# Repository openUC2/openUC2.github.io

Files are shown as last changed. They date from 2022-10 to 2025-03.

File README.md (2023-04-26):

# openUC2 Documentation

This is the repository where you will find all kinds of documents, tutorials and helping functions to get started with UC2.

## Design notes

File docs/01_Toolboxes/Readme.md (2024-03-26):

# Educational Kits

## CoreBox: Entry-Level Education Box
     - Features and Specifications
     - Assembling the CoreBox
     - Core Lens, Telescope, and Microscope

## Discovery Kit: Extension of CoreBox
     - Adding Modules to the Discovery Kit
     - Enhanced Functionality

## Interferometer Kit 
     - You can build a Michelson Interferometer
     - Try enhancing it to become a MAch Zhender Microscope 
     - Ultimatively test the microscope extension and reconstruct images using holography
     -

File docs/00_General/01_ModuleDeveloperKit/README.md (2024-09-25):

# openUC2 Template for your own Insert

We try to keep UC2 as open as possible. One important step is to give you the tools at hand to create your own insert in Order to add own functionalities, parts, modules, etc.
This repository should help you creating inserts and understand the core idea behind the shape and how it can be used to add e.g. lenses, mirros, motors.

If you have a more complex idea for a module, say a rotating diffuser, please feel free to reach out to us! We are happy to support your research with open-source tools!

A good resource is also the [***Module Developer Kit (MDK)***](https://github.com/openUC2/UC2-GIT/tree/master/MDK) that summarizes the core concept of UC2's modularity.

***What you will see here:***

* UC2 Cube Inserts
* Design files for
	* Autodesk Inventor
	* OpenSCAD
	* Fusion360
	* STP- and STL-files
* Technical drawings to replicate module in e.g. metal?
* Tutorial to design your modules in Autodesk

## UC2 v3 Design

## Fusion360 Design Files

### Cube and Base

This is a close-to-the-injection-molding design. The press-fit can vary. It's optimized for 3D printing.

You can find the latest Inventor Design files in the Fusion360 cloud: https://a360.co/3ZwHhl7

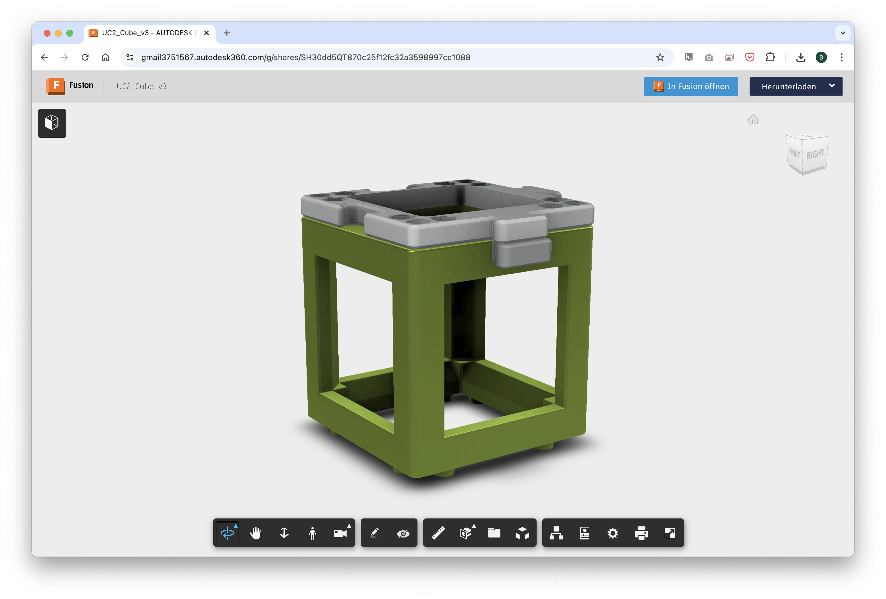
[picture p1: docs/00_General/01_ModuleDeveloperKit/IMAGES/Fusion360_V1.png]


You can download and export this in multiple CAD formats.

### Insert

This serves as a template for your optics. Fill it with whatever you have and model it in your 3D CAD software: https://a360.co/3MYo0RX

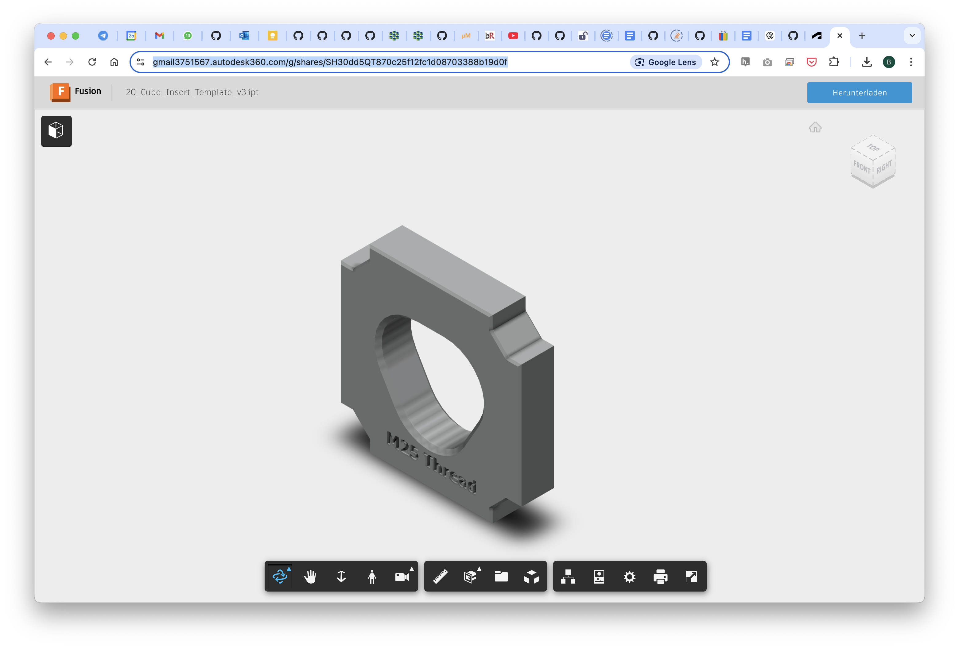
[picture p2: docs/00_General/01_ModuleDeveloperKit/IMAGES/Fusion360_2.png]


### UC2 Cube Inserts

The cube inserts can be fully customized to adapt any optical element to the cubes. So far a perpendicular and diagonal version exists. The design files for Autodesk Inventor and OpenSCAD are available. Once you have a customized version, please share it so that the open-aspect of the system reaches its full potential :)

A Youtube tutorial showing you how to create your own insert can be found [here](https://youtu.be/CUzuymscB5k)

Since the cube is point symmetric around the origin, the inserts can be rotated in all directions and bridges external components to the modules by acting as an open-standard.

When you create a new insert, you have to make sure it follows the following design criteria (e.g. dimensions):

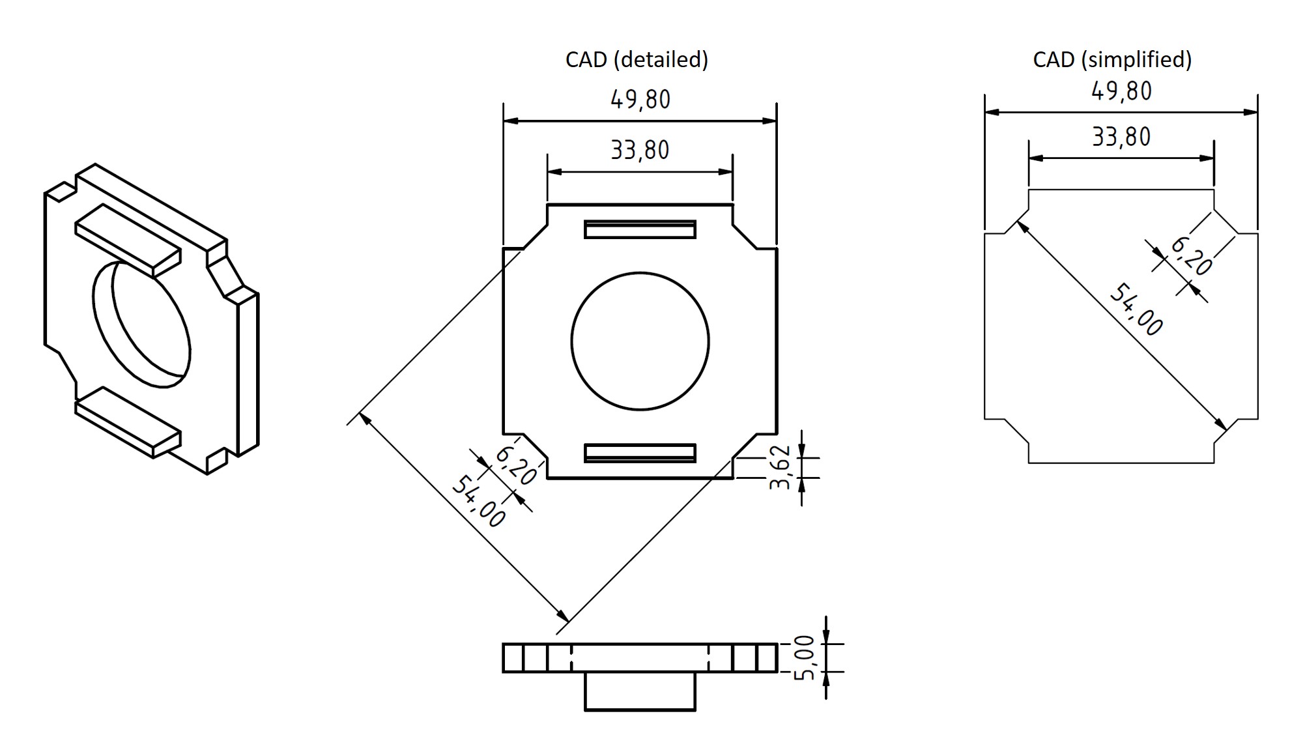
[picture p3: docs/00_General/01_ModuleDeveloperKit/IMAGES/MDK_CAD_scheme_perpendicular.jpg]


For the baseplate you must follow these dimensions:

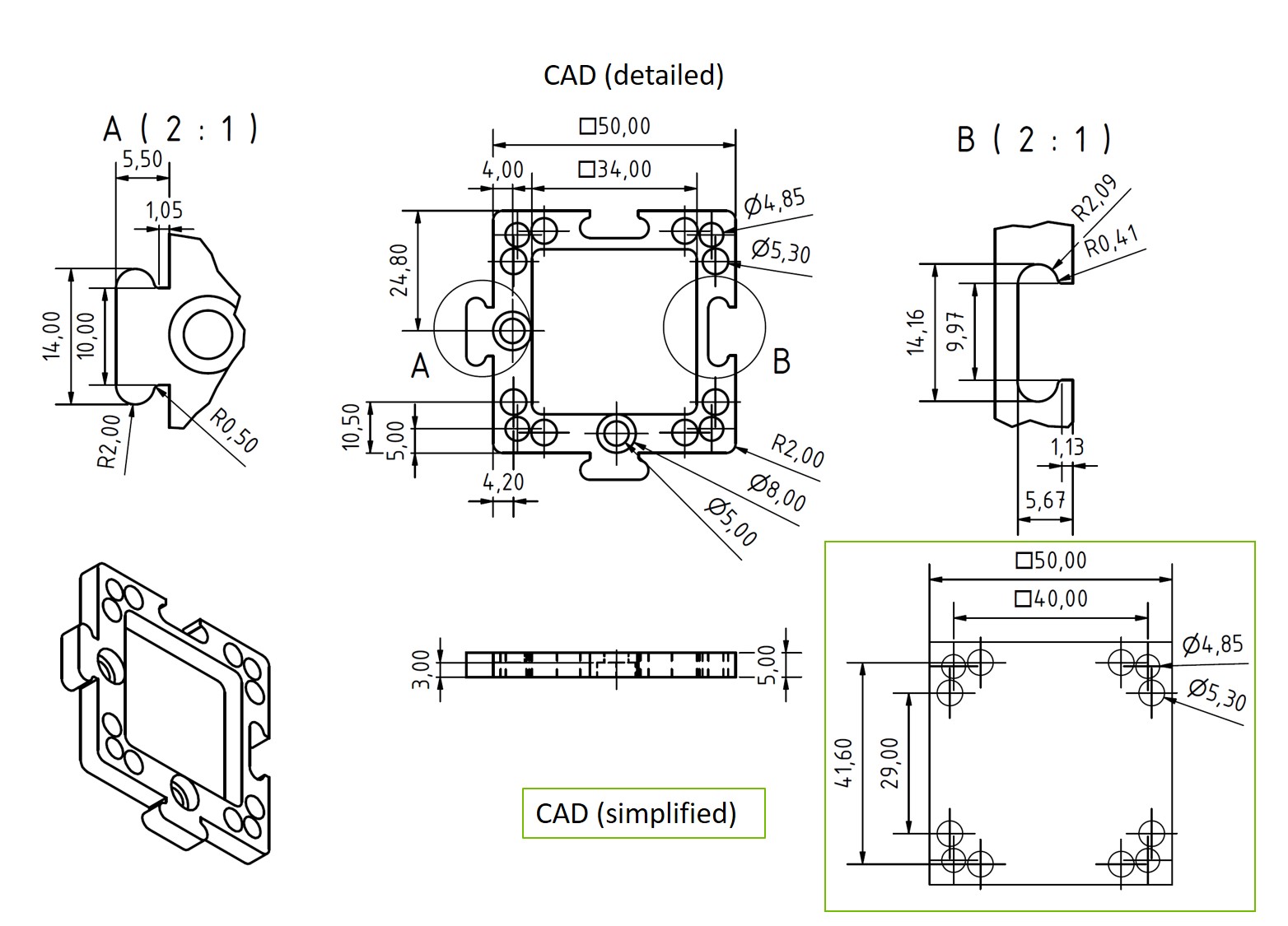
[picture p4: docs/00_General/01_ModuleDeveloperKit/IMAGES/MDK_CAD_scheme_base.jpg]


The CAD templates for Autodesk Inventor 2022 (```.ipt```) and ```STL/STEP```-standard can be found in the [INVENTOR](./INVENTOR)-folder and  [STL](./STL)/ [STP](./STP)-folder .

## Autodesk Inventor 2022 Design files

All files can be found in the folder [INVENTOR](./INVENTOR).

***Steps to work on the files:***

1. Open Autodesk Inventor 2022
2. Create a new project
3. Open the Assembly file: `Assembly_Cube_Template_v3.iam`
4. Get yourself familiar with the:
- Cube
- Baseplate
- Insert
5. Try modifying the file `20_Cube_Insert_Template_v3.ipt` so that you can mount your inidividual files

### Videotutorial

We have a dedicated video tutorial to show how you can create your own insert.
**Video Tutorial on How to design a Cube Insert (Perpendicular to the optical axis)**  
**The tutorial shows a v2 insert - the principle is the same but the dimensions differ!**

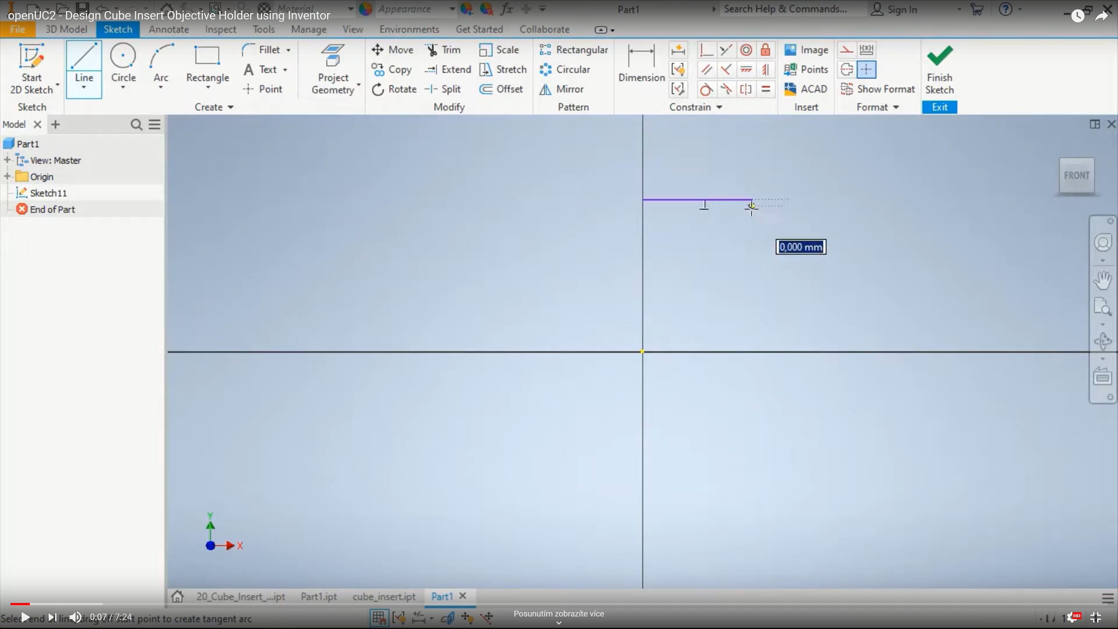
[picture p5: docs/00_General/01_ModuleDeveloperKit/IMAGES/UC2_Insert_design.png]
UC2 YouSeeToo - How to design an insert (https://www.youtube.com/watch?v=q2DNw-Q1KEo&t=2s)


## OpenSCAD Design files

All files can be found in the folder [OPENSCAD](./OPENSCAD).

*Alternatively* you can also find the files in the Thingiverse Universe that allows you to modify certain parameters in the file without installing openSCAD. You can find it here [Thingiverse](https://www.thingiverse.com/openuc2/designs).

***Steps to work on the files:***

1. Open OpenSCAD
2. Open the file `UC2_Lens_insert_v2.scad`
3. Try to understand what each parameter modifies in the geometry of the cube insert
4. Render and export as STL

## Technical Drawings

You can find additional information about the cube in the folder [CAD](./CAD).

### CAD file for the cube (injection molded / IM)

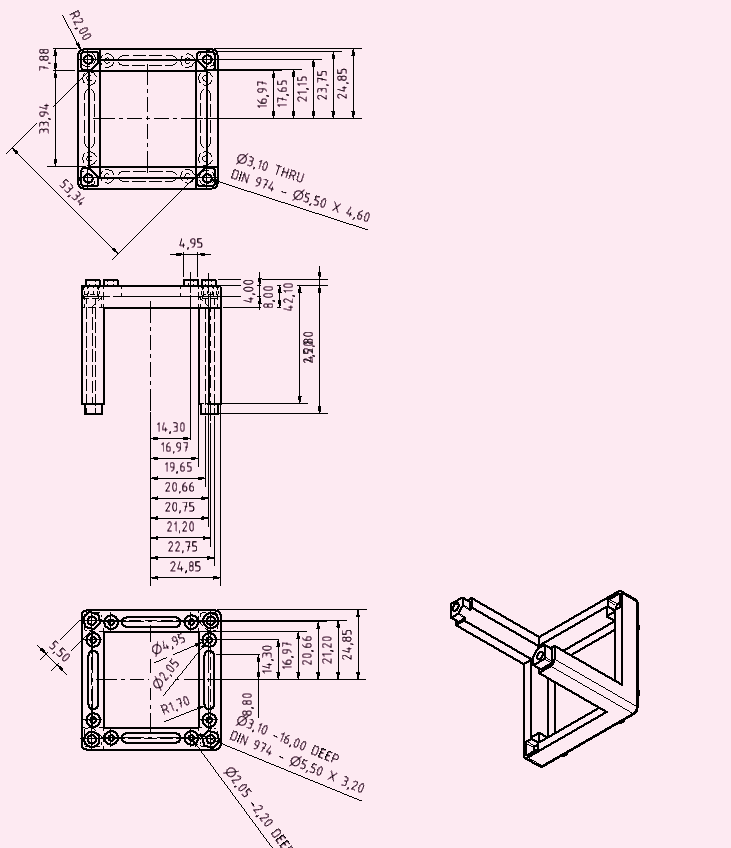
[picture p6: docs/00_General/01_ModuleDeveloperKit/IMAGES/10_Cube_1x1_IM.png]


## Get Involved

This project is open so that anyone can get involved. You don't even have to learn CAD designing or programming. Find ways you can contribute in  [CONTRIBUTING](https://github.com/openUC2/UC2-GIT/blob/master/CONTRIBUTING.md)

## License and Collaboration

This project is open-source and is released under the CERN open hardware license. Our aim is to make the kits commercially available.
We encourage everyone who is using our Toolbox to share their results and ideas, so that the Toolbox keeps improving. It should serve as a easy-to-use and easy-to-access general purpose building block solution for the area of STEAM education. All the design files are generally for free, but we would like to hear from you how is it going.

You're free to fork the project and enhance it. If you have any suggestions to improve it or add any additional functions make a pull-request or file an issue.

Please find the type of licenses [here](https://github.com/openUC2/UC2-GIT/blob/master/License.md)

REMARK: All files have been designed using Autodesk Inventor 2019 (EDUCATION)

## Collaborating
If you find this project useful, please like this repository, follow us on Twitter and cite the webpage! :-)

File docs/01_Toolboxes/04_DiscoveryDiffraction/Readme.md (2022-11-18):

# Building The CourseBOX

This is a guide for building the [CourseBOX](../). If you were looking for another BOX version, [click here](../../).

This guide currently describes how to build both the [finite-corrected version](#finite-corrected-optics) and the [infinity version](#inifinity-optics) of the CourseBOX.

### Content of each section
1. Shopping
1. 3D printing
1. Tools
1. Assembly

# Infinity Optics

* Total price: 300 € without a Raspberry Pi (190 €) (assuming only material costs and printing everything yourself)
* Printing time including preparation: 4 days
* Assembly time: 1 day

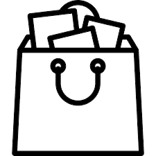
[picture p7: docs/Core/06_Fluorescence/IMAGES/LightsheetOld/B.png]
##  Shopping
### What to buy
* Check out the [RESOURCES](../../../TUTORIALS/RESOURCES) for more information!

Link - name of part             |  Amount |  Comment | Price
  :-------------------------:|:----------------------------:|:-------------------------:|:-------------------------:
  3D printing material|~580 g| Choose material that works with your 3D printer. If unsure, have a look at the guide in 3D printing section|15 €
  [Lens 50 mm](https://www.thorlabs.com/thorproduct.cfm?partnumber=LA1131)  |  5 pieces ||á 21 €
  [Lens 100 mm](https://optikbaukasten.de/)  |  3 pieces |Artikel 2004|á 6 €
  [Lens for Eye Cube](https://www.pgi-versand.de/?id=47&mode=artdet&artnr=551.OAL)  |  1 piece |551.OAL|á 5 €
  [Beamsplitter](https://optikbaukasten.de/)  |  1 piece |Artikel 2137|á 27 €
  [Flashlight](https://www.pollin.de/p/led-taschenlampe-alu-5-w-cree-led-3xmicro-schwarz-b-ware-535448)  |  1 piece | Light source for microscope.|á 7 €
  [Laser Pointer](https://www.conrad.de/de/p/ansmann-laserpointer-2in1-reichweite-max-im-freifeld-50-m-2162622.html)  |  1 piece | Light source for the Abbe experiment. With this very one you don't even need the flashlight. More information below.|á 5 €
  [Magnets](https://www.magnetladen.de/kugelmagnet-5-mm-n42-nickel/)  |  64 pieces | When using 3DP Cubes and baseplates. Ball magnets, diameter 5 mm.|total 20 €
  [Screws](https://eshop.wuerth.de) |   7 pieces | M2×16 - 6 pieces; M2 nut - 6 pieces; M3×18 - 4 pieces | total ~2 €
  [Screws](https://eshop.wuerth.de) |   112 pieces | For 3DP Cubes extra: (Art.-Nr. 00843  12) M3×12, galvanized steel - 64  pieces; (Art.-Nr. 00843  8) M3×8, galvanized steel - 64 pieces (or 128 pieces of M3×12) - BUT for this setup it isn't necessary to have screws on both sides ; (Art.-Nr. 025505 8) M5×8, galvanized steel - 96  pieces (half if one-sided) | total ~4 €
  Raspberry Pi with accessories ||Have a look in our [Bill-of-Materials](https://docs.google.com/spreadsheets/d/1U1MndGKRCs0LKE5W8VGreCv9DJbQVQv7O6kgLlB6ZmE/edit?usp=sharing) for a complete list and links. | 190 €
  [Chocolate](https://prod-cd-origin.milka.de/produkte/milka-weisse-schokolade)|1 bar| Use it as a reward when you're done.

#### 2 in 1 light source
We propose the use of this [Laser Pointer](https://www.conrad.de/de/p/ansmann-laserpointer-2in1-reichweite-max-im-freifeld-50-m-2162622.html), because it also has a white LED. But we need to smartly adapt this for our experiments.
* For beam expansion of the laser light, print a laser cap from the STL folder and put in it the RasPi lens that you removed from the camera
* The LED here has a lens which cannot be removed. To be able to find a focussed image of your light source, take a thin permanent marker and make a cross on the surface of this lens. Now you'll be able to see a focussed image of the cross in the Field set of Aperture planes
<p align="center">



</p>

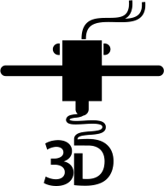
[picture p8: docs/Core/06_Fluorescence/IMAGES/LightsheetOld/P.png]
##  3D Printing:
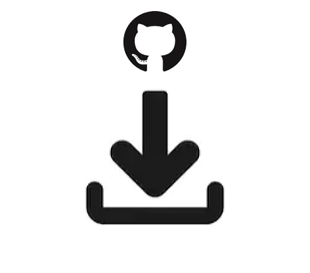
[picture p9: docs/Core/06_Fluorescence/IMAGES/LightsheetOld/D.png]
### Parts
To acquire the STL-files use the [UC2-Configurator](https://uc2configurator.netlify.app/). The files themselves are in the [RAW](../../../CAD/RAW/STL) folder. The BOXes can be built using injection-moulded (IM) or 3D-printed (3DP) cubes.

Note on the lens holders: If you use some other lens, you can generate a holder for it using our openSCAD design. Go to the [Thingiverse page of this lens holder](https://www.thingiverse.com/thing:4377691) and use their in-built customizer to change the parameters of the insert.

Completely new to 3D printing? Have a look into this [beginner's guide](https://www.makeuseof.com/tag/beginners-guide-3d-printing/)!

Our quick printing tutorial can be found here:
UC2 YouSeeToo - How to print the base-cube? (https://www.youtube.com/watch?v=SblqYJYXe4k&feature=youtu.be)

We have a good experience with this printer and settings:
* Prusa i3/MK3S
  * Prusament PLA 1,75 mm, for one Box: 0,58 kg = 195 m = 90 hours = 15 €
  * Profile Optimal 0,15 mm, infill 20%, no support, 215/60°C

## Which tools to use
Tool             |  Image|  Comment
:-------------------------:|:----------------------------:|:-------------------------:
[Electric screw driver with 2,5 mm hex bit](https://www.amazon.de/Bosch-Akkuschrauber-Generation-Bits-Ladeger%C3%A4t/dp/B00TTZU566/ref=asc_df_B00TTZU566/?tag=googshopde-21&linkCode=df0&hvadid=255989693737&hvpos=1o1&hvnetw=g&hvrand=6125749874385941808&hvpone=&hvptwo=&hvqmt=&hvdev=c&hvdvcmdl=&hvlocint=&hvlocphy=9042960&hvtargid=pla-421346020200&psc=1&th=1&psc=1) |[](https://www.amazon.de/Bosch-Akkuschrauber-Generation-Bits-Ladeger%C3%A4t/dp/B00TTZU566/ref=asc_df_B00TTZU566/?tag=googshopde-21&linkCode=df0&hvadid=255989693737&hvpos=1o1&hvnetw=g&hvrand=6125749874385941808&hvpone=&hvptwo=&hvqmt=&hvdev=c&hvdvcmdl=&hvlocint=&hvlocphy=9042960&hvtargid=pla-421346020200&psc=1&th=1&psc=1) | For putting the cubes together using M3×12 and M3×8 screws.
[2,5 mm hex key](https://www.amazon.de/Presch-Innensechskant-Satz-Kugelkopf-Innensechskantschl%C3%BCssel/dp/B079V335CR/ref=sr_1_2_sspa?__mk_de_DE=%C3%85M%C3%85%C5%BD%C3%95%C3%91&crid=2K89GU3MY8P26&keywords=hex+key+set&qid=1575997133&s=diy&sprefix=hex+%2Cdiy%2C160&sr=1-2-spons&psc=1&spLa=ZW5jcnlwdGVkUXVhbGlmaWVyPUEzRENMU0hKWkJRR0FEJmVuY3J5cHRlZElkPUEwMDIzMjIyMzFBWVIyOEpORU1FSCZlbmNyeXB0ZWRBZElkPUEwMzk0NjQwMlA0NFZDTVk0Tk9LUSZ3aWRnZXROYW1lPXNwX2F0ZiZhY3Rpb249Y2xpY2tSZWRpcmVjdCZkb05vdExvZ0NsaWNrPXRydWU=) | [](https://www.amazon.de/Presch-Innensechskant-Satz-Kugelkopf-Innensechskantschl%C3%BCssel/dp/B079V335CR/ref=sr_1_2_sspa?__mk_de_DE=%C3%85M%C3%85%C5%BD%C3%95%C3%91&crid=2K89GU3MY8P26&keywords=hex+key+set&qid=1575997133&s=diy&sprefix=hex+%2Cdiy%2C160&sr=1-2-spons&psc=1&spLa=ZW5jcnlwdGVkUXVhbGlmaWVyPUEzRENMU0hKWkJRR0FEJmVuY3J5cHRlZElkPUEwMDIzMjIyMzFBWVIyOEpORU1FSCZlbmNyeXB0ZWRBZElkPUEwMzk0NjQwMlA0NFZDTVk0Tk9LUSZ3aWRnZXROYW1lPXNwX2F0ZiZhY3Rpb249Y2xpY2tSZWRpcmVjdCZkb05vdExvZ0NsaWNrPXRydWU=)| For fine adjustment of all the M3 screws if needed.
[Needle-nose Pliers](https://www.amazon.de/Br%C3%BCder-Mannesmann-Telefonzange-gerade-M10948/dp/B003A63EIG/ref=sr_1_3?__mk_de_DE=%C3%85M%C3%85%C5%BD%C3%95%C3%91&keywords=needle+nose+pliers&qid=1575997091&s=diy&sr=1-3) |[](https://www.amazon.de/Br%C3%BCder-Mannesmann-Telefonzange-gerade-M10948/dp/B003A63EIG/ref=sr_1_3?__mk_de_DE=%C3%85M%C3%85%C5%BD%C3%95%C3%91&keywords=needle+nose+pliers&qid=1575997091&s=diy&sr=1-3) | Might come handy

## Assembly
Part - link             |  Result|  Comment
:-------------------------:|:----------------------------:|:-------------------------:
[Baseplates](../../../CAD/ASSEMBLY_Baseplate)|[](../../../CAD/ASSEMBLY_Baseplate)|16× baseplate puzzle
[Lens Cubes](../../../CAD/ASSEMBLY_CUBE_Lens)|[](../../../CAD/ASSEMBLY_CUBE_Lens)| 8× Lens Cube: 5× Lens Cube with 50 mm lens; 3× Lens Cube with 100 mm lens.
[Sample Cubes](../../../CAD/ASSEMBLY_CUBE_Sample_Holder)|[](../../../CAD/ASSEMBLY_CUBE_Sample_Holder)|2× Sample Holder Cube
[Flashlight Cube](../../../CAD/ASSEMBLY_CUBE_Flashlight)|[](../../../CAD/ASSEMBLY_CUBE_Flashlight)| 1× Flashlight Cube
[Circular Aperture Cube](../../../CAD/ASSEMBLY_CUBE_Aperture_Circular)|[](../../../CAD/ASSEMBLY_CUBE_Aperture_Circular)|2× Circular Aperture Cube
[Rectangular Aperture Cube](../../../CAD/ASSEMBLY_CUBE_Aperture_Rectangular)|[](../../../CAD/ASSEMBLY_CUBE_Aperture_Rectangular)|1× Rectangular Aperture Cube
[Beamsplitter Cube](../../../CAD/ASSEMBLY_CUBE_Beamsplitter)|[](../../../CAD/ASSEMBLY_CUBE_Beamsplitter)|1× Beam Expander Cube
[RasPi Camera Cube](../../../CAD/ASSEMBLY_CUBE_RaspiCam)|[](../../../CAD/ASSEMBLY_CUBE_RaspiCam)|1× Camera Cube with Raspberry Pi camera with the lens removed
[Laser Cube](../../../CAD/ASSEMBLY_CUBE_Laser)|[](../../../CAD/ASSEMBLY_CUBE_Laser)|1× Laser Holder Cube and Laser Clamp with a cap for RasPi lens
[Eye Cube](../../../CAD/ASSEMBLY_CUBE_Eyeball)|[](../../../CAD/ASSEMBLY_CUBE_Eyeball)|1× Eyeball Cube  

## Software
Prepare the Raspberry Pi following our [tutorial in UC2-Software-GIT](https://github.com/bionanoimaging/UC2-Software-GIT/tree/master/GUI/RASPBERRY_PI)!

##  Done! Great job!

---

# Finite-corrected Optics

* Printing time including preparation: 5 days
* Assembly time: 1 day

## Shopping
### What to buy
* Check out the [RESOURCES](../../../TUTORIALS/RESOURCES) for more information!

Link - name of part             |  Amount |  Comment | Price per amount used
  :-------------------------:|:----------------------------:|:-------------------------:|:-------------------------:
  3D printing material|~620 g| Choose material that works with your 3D printer. If unsure, have a look at the guide in 3D printing section|20 €
  [Microscope objective 4×](https://de.aliexpress.com/item/32947647522.html?spm=a2g0x.search0104.3.54.6cf57a4c3DwsTO&transAbTest=ae803_3&ws_ab_test=searchweb0_0%2Csearchweb201602_6_10065_10130_10068_10890_10547_319_10546_317_10548_10545_10696_10084_453_454_10083_10618_10307_537_536_10902_10059_10884_10887_321_322_10103%2Csearchweb201603_6%2CppcSwitch_0&algo_pvid=06d972be-b176-4446-8665-56d9e61a8d2c&algo_expid=06d972be-b176-4446-8665-56d9e61a8d2c-7)  |  1 piece | | 10 €
  [Lens 35 mm](https://www.thorlabs.com/thorproduct.cfm?partnumber=LA1027)  |  1 piece |We did the alignment with lenses of these focal lengths, but other combination are also possible. The alignment principle stays the same, but the positions of the element will be different. |22 €
  [Lens 40 mm](https://www.thorlabs.com/thorproduct.cfm?partnumber=LA1422)  |  2 pieces ||44 €
  [Lens 50 mm](https://www.thorlabs.com/thorproduct.cfm?partnumber=LA1131)  |  1 piece ||21 €
  [Lens 75 mm](https://www.thorlabs.com/thorproduct.cfm?partnumber=LA1608)  |  1 piece ||20 €
  [Lens 100 mm](https://www.thorlabs.com/thorproduct.cfm?partnumber=LA1509)  |  1 piece ||20 €
  [Flashlight](https://www.pollin.de/p/led-taschenlampe-alu-5-w-cree-led-3xmicro-schwarz-b-ware-535448)  |  1 piece | Light source for the projector and microscope.|7 €
  [Magnets](https://www.magnetladen.de/kugelmagnet-5-mm-n42-nickel/)  |  128 pieces | Ball magnets, diameter 5 mm.|30 €
  [Screws](https://eshop.wuerth.de/Zylinderschraube-mit-Innensechskant-SHR-ZYL-ISO4762-88-IS25-A2K-M3X12/00843%20%2012.sku/de/DE/EUR/) |   ~120 pieces | M3×12, galvanized steel - ~90  pieces; M3×8, galvanized steel - ~90 pieces; M3×18, galvanized steel - 2 pieces; M3×30, not magnetic - 1 piece; M3 nut | ~15 €
  [Chocolate](https://prod-cd-origin.milka.de/produkte/milka-weisse-schokolade)|1 bar| Use it as a reward when you're done.

##  3D Printing:

Completely new to 3D printing? Have a look into this [beginner's guide](https://www.makeuseof.com/tag/beginners-guide-3d-printing/)!

Our quick printing tutorial can be found here:
UC2 YouSeeToo - How to print the base-cube? (https://www.youtube.com/watch?v=SblqYJYXe4k&feature=youtu.be)

We have a good experience with this printer and settings:
* Prusa i3/MK3S
  * PLA 1,75 mm, for one Box: 0,6 kg = 235 m = 85 hours = 20 €
  * Profile Optimal 0,15 mm, infill 20%, no support, 215/60°C

### Note: The design of the mechanical Z-stage has recently been changed. The files here are not yet up-to-date. Please check the [Mechanical Z-stage](../../../CAD/ASSEMBLY_CUBE_Z-STAGE_mechanical_v2) for the latest version. Same applies to the Lens Holder available [here](../../../CAD/ASSEMBLY_CUBE_Lens_v2)

###  Housing
Name of part - Link to STL file             |  Amount
:-------------------------:|:----------------------------:
[(01) Basic Cube 2×1](./STL/01_10_Cube_2x1_v2.stl)  |  1 piece
[(02) Basic Lid 2×1](./STL/02_10_Lid_el_2x1_v2.stl)  |  1 piece
[(03) Basic Cube 1×1](./STL/03_10_Cube_1x1_v2.stl)  |  20 pieces
[(04) Basic Lid 1×1](./STL/04_10_Lid_1x1_v2.stl)  |  20 pieces
[(05) Baseplate 4×1](./STL/05_Assembly_base_4x1.stl)  |  4 pieces
[(06) Baseplate 4×2](./STL/06_Assembly_base_4x2.stl)  |  1 piece
[(07) Baseplate 1×1](./STL/07_10_Base_v2.stl)  |  1 piece
[(08) Baseplate Connector 1×1](./STL/08_Baseplate_Connector_v2.stl)  |  1 piece

###  Inserts

Name of part - Link to STL file            |  Amount |  Comment
:-------------------------:|:-------------------------:|:-------------------------:
[(09) Z-Stage Focusing Insert](./STL/09_20_focus_inlet_linearflexure_v0_1.stl)  |  1 piece  | Rotate the part in your slicer before printing. Always print it laying on the flat side.
[(10) Z-Stage Objective Mount](./STL/10_30_focus_inlet_objective_mount_v7_7.stl) |  1 piece   | For mounting the objective lens (RMS thread).
[(11a) Z-Stage Bottom Plate](./STL/11a_20_focus_inlet_plate_bottom_2.stl) |  1 piece   | The plate holds the gear and screw in position, allowing the only to rotate but not to wobble.
[(11b) Z-Stage Top Plate](./STL/11b_20_focus_inlet_plate_top_3.stl) |  1 piece   | The plate holds the gear and screw in position, allowing the only to rotate but not to wobble.
[(12) Z-Stage Gear](./STL/12_20_focus_inlet_gear.stl) |  1 piece   | Kindly borrowed from [openflexure](https://openflexure.org).
[(13) Lens Holder](./STL/13_1inch_Assembly_Insert_Lens_mount_fixed_20_Lens_holder.stl)  |  6 pieces | Diameter fits for the listed lenses (25 mm).
[(14) Lens Holder Clamp](./STL/14_1inch_Assembly_Insert_Lens_mount_fixed_20_Lens_holder_clamp.stl)  |  6 pieces | Diameter fits for the listed lenses (25 mm).
[(15) Cylindrical Lens Holder](./STL/15_20_Cube_Insert_Lens_Cylindrical.stl)  |  1 piece | Diameter fits for the listed lenses (25 mm).
[(16) Generic Sample Holder](./STL/16_20_Cube_insert_Sample_holder.stl)  |  5 pieces | In the SimpleBOX, it is used to hold the object in the projector setup.
[(17) Generic Sample Holder Clamp](./STL/17_20_Cube_Insert_Sample_clamp.stl)  |  5 pieces | To fix the sample.
[(18) Mirror Holder 45° 30×30mm²](./STL/18_20_Cube_Insert_Mirror_Holder_30x30Mirror_v2.stl)  |  1 piece | Size fits for the listed mirrors.
[(19) Flashlight Holder](./STL/19_20_Cube_Insert_Flashlight_Holder.stl)  |  2 pieces |
[(20) Circular Aperture Guide](./STL/20_20_Cube_Insert_CirAp_Guide.stl)  |  2 pieces |
[(21) Circular Aperture Wheel](./STL/21_20_Cube_Insert_CirAp_Wheel.stl)  |  2 pieces |
[(22) Circular Aperture Lid](./STL/22_20_Cube_Insert_CirAp_Lid.stl)  |  2 pieces |
[(23) Circular Aperture Leaf](./STL/23_20_Cube_Insert_CirAp_Leaf1.stl)  |  14 pieces |
[(24) Laser Holder](./STL/24_20_Cube_Insert_Laser_Mount.stl)  |  2 pieces |
[(25) Laser Clamp](./STL/25_00_Laser_Clamp_OnOffSwitch.stl)  |  1 piece |
[(26) Beam Expander Insert](./STL/26_20_Cube_Insert_Beamexpander.stl)  |  1 piece |
[(27) Beam Expander Lens Adapter](./STL/27_30_Lens_Adapter_Beamexpander.stl)  |  1 piece |
[(28) Beamsplitter Insert](./STL/28_20_Cube_Insert_Beamsplitter.stl)  |  1 piece |

## Which tools to use
Tool             |  Image|  Comment
:-------------------------:|:----------------------------:|:-------------------------:
[Electric screw driver with 2,5 mm hex bit](https://www.amazon.de/Bosch-Akkuschrauber-Generation-Bits-Ladeger%C3%A4t/dp/B00TTZU566/ref=asc_df_B00TTZU566/?tag=googshopde-21&linkCode=df0&hvadid=255989693737&hvpos=1o1&hvnetw=g&hvrand=6125749874385941808&hvpone=&hvptwo=&hvqmt=&hvdev=c&hvdvcmdl=&hvlocint=&hvlocphy=9042960&hvtargid=pla-421346020200&psc=1&th=1&psc=1) |[](https://www.amazon.de/Bosch-Akkuschrauber-Generation-Bits-Ladeger%C3%A4t/dp/B00TTZU566/ref=asc_df_B00TTZU566/?tag=googshopde-21&linkCode=df0&hvadid=255989693737&hvpos=1o1&hvnetw=g&hvrand=6125749874385941808&hvpone=&hvptwo=&hvqmt=&hvdev=c&hvdvcmdl=&hvlocint=&hvlocphy=9042960&hvtargid=pla-421346020200&psc=1&th=1&psc=1) | For putting the cubes together using M3×12 and M3×8 screws.
[2,5 mm hex key](https://www.amazon.de/Presch-Innensechskant-Satz-Kugelkopf-Innensechskantschl%C3%BCssel/dp/B079V335CR/ref=sr_1_2_sspa?__mk_de_DE=%C3%85M%C3%85%C5%BD%C3%95%C3%91&crid=2K89GU3MY8P26&keywords=hex+key+set&qid=1575997133&s=diy&sprefix=hex+%2Cdiy%2C160&sr=1-2-spons&psc=1&spLa=ZW5jcnlwdGVkUXVhbGlmaWVyPUEzRENMU0hKWkJRR0FEJmVuY3J5cHRlZElkPUEwMDIzMjIyMzFBWVIyOEpORU1FSCZlbmNyeXB0ZWRBZElkPUEwMzk0NjQwMlA0NFZDTVk0Tk9LUSZ3aWRnZXROYW1lPXNwX2F0ZiZhY3Rpb249Y2xpY2tSZWRpcmVjdCZkb05vdExvZ0NsaWNrPXRydWU=) | [](https://www.amazon.de/Presch-Innensechskant-Satz-Kugelkopf-Innensechskantschl%C3%BCssel/dp/B079V335CR/ref=sr_1_2_sspa?__mk_de_DE=%C3%85M%C3%85%C5%BD%C3%95%C3%91&crid=2K89GU3MY8P26&keywords=hex+key+set&qid=1575997133&s=diy&sprefix=hex+%2Cdiy%2C160&sr=1-2-spons&psc=1&spLa=ZW5jcnlwdGVkUXVhbGlmaWVyPUEzRENMU0hKWkJRR0FEJmVuY3J5cHRlZElkPUEwMDIzMjIyMzFBWVIyOEpORU1FSCZlbmNyeXB0ZWRBZElkPUEwMzk0NjQwMlA0NFZDTVk0Tk9LUSZ3aWRnZXROYW1lPXNwX2F0ZiZhY3Rpb249Y2xpY2tSZWRpcmVjdCZkb05vdExvZ0NsaWNrPXRydWU=)| For fine adjustment of all the M3 screws if needed.
[1,5 mm hex key](https://www.amazon.de/Presch-Innensechskant-Satz-Kugelkopf-Innensechskantschl%C3%BCssel/dp/B079V335CR/ref=sr_1_2_sspa?__mk_de_DE=%C3%85M%C3%85%C5%BD%C3%95%C3%91&crid=2K89GU3MY8P26&keywords=hex+key+set&qid=1575997133&s=diy&sprefix=hex+%2Cdiy%2C160&sr=1-2-spons&psc=1&spLa=ZW5jcnlwdGVkUXVhbGlmaWVyPUEzRENMU0hKWkJRR0FEJmVuY3J5cHRlZElkPUEwMDIzMjIyMzFBWVIyOEpORU1FSCZlbmNyeXB0ZWRBZElkPUEwMzk0NjQwMlA0NFZDTVk0Tk9LUSZ3aWRnZXROYW1lPXNwX2F0ZiZhY3Rpb249Y2xpY2tSZWRpcmVjdCZkb05vdExvZ0NsaWNrPXRydWU=) |↑↑ | For mounting worm screws.
[Needle-nose Pliers](https://www.amazon.de/Br%C3%BCder-Mannesmann-Telefonzange-gerade-M10948/dp/B003A63EIG/ref=sr_1_3?__mk_de_DE=%C3%85M%C3%85%C5%BD%C3%95%C3%91&keywords=needle+nose+pliers&qid=1575997091&s=diy&sr=1-3) |[](https://www.amazon.de/Br%C3%BCder-Mannesmann-Telefonzange-gerade-M10948/dp/B003A63EIG/ref=sr_1_3?__mk_de_DE=%C3%85M%C3%85%C5%BD%C3%95%C3%91&keywords=needle+nose+pliers&qid=1575997091&s=diy&sr=1-3) | Might come handy

##   Assembly
Part - link             |  Result|  Comment
:-------------------------:|:----------------------------:|:-------------------------:
[Baseplates](../../../CAD/ASSEMBLY_Baseplate)|[](../../../CAD/ASSEMBLY_Baseplate)|1× "big" baseplate (4×2), 4× "small" baseplate (4×1), 1× "unit" baseplate (1×1), 1× "unit" baseplate connector (1×1)
[Z-Stage Cube](../../../CAD/ASSEMBLY_CUBE_Z-STAGE_mechanical)|[](../../../CAD/ASSEMBLY_CUBE_Z-STAGE_mechanical)|1× mechanical Z-Stage, Sample Clamp not necessary
[Lens Cubes](../../../CAD/ASSEMBLY_CUBE_Lens)|[](../../../CAD/ASSEMBLY_CUBE_Lens)| 6× Lens Cube; Write the focal lengths of the lenses on the holders, so you can always easily find the right one when building the setups.
[Cylindrical Lens Cube](../../../CAD/ASSEMBLY_CUBE_Lens_CYLINDRICAL)|[](../../../CAD/ASSEMBLY_CUBE_Lens_CYLINDRICAL)| 1× Cylindrical Lens Cube
[Sample Cubes](../../../CAD/ASSEMBLY_CUBE_Sample_Holder)|[](../../../CAD/ASSEMBLY_CUBE_Sample_Holder)|5× Sample Holder Cube
[Mirror Cube](../../../CAD/ASSEMBLY_CUBE_Mirror_45)|[](../../../CAD/ASSEMBLY_CUBE_Mirror_45)| 1× Mirror Cube
[Flashlight Cube](../../../CAD/ASSEMBLY_CUBE_Flashlight)|[](../../../CAD/ASSEMBLY_CUBE_Flashlight)| 1× Flashlight Cube
[Circular Aperture Cube](../../../CAD/ASSEMBLY_CUBE_Aperture_Circular)|[](../../../CAD/ASSEMBLY_CUBE_Aperture_Circular)|2× Circular Aperture Cube
[Laser Cube](../../../CAD/ASSEMBLY_CUBE_Laser)|[](../../../CAD/ASSEMBLY_CUBE_Laser)|1× Laser Holder Cube and Laser Clamp
[Beam Expander Cube](../../../CAD/ASSEMBLY_CUBE_Beamexpander)|[](../../../CAD/ASSEMBLY_CUBE_Beamexpander)|1× Beam Expander Cube
[Beamsplitter Cube](../../../CAD/ASSEMBLY_CUBE_Beamsplitter)|[](../../../CAD/ASSEMBLY_CUBE_Beamsplitter)|1× Beam Expander Cube

## Done! Great job!

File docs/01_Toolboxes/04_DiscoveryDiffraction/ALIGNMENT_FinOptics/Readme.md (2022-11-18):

# The Course BOX Alignment Procedure (Finite Optics)
This is the alignment procedure of the experiments with finite-corrected optics. If you are looking for the infinity-corrected setups [click here](../ALIGNMENT_InfOptics).

### First experiment: Finite-corrected Microscope with Köhler Illumination
This experiment demonstrates the essential parts of a microscope and explains the concept of conjugate planes. The key components are: Light source, Collector lens, Field Diaphragm, Aperture Diaphragm, Condenser lens, Sample, Objective lens and Eyepiece lens.
<p align="center">

</p>
The Aperture set of conjugate planes: Lamp filament, Aperture diaphragm, Back Focal Plane of the objective, Exit pupil of the eye.
<p align="center">

</p>
The Field set of conjugate planes: Field diaphragm, Sample plane, Primary Image Plane, Retina.
<p align="center">

</p>

### Second experiment: Abbe Diffraction Experiment
The famous Abbe Diffraction Experiments shows how diffraction of light by a specimen (and interference with the illuminating light) creates an image and how collection of diffracted light defines the resolution of the microscope. With this setup it is possible to view both sets of conjugate planes at the same time, with one's eye or a camera.
<p align="center">

</p>
The Aperture set of conjugate planes: Lamp filament, Aperture diaphragm, Back Focal Plane of the objective, Mirror surface in the side arm, Retina.
<p align="center">

</p>
The Field set of conjugate planes: Field diaphragm, Sample plane, Primary Image Plan, Retina.
<p align="center">

</p>
We propose to use a diffraction grating as a sample and spatial filter in the BFP.

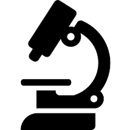
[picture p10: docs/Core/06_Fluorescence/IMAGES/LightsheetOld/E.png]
##  This tutorial will lead you step-by-step through the alignment of the Finite-corrected Microscope, Köhler Illumination and Abbe Diffraction Experiment.

1. Start with 1×13 baseplate and all the cubes:

* Flashlight Cube (1)
* Collector Lens Cube (2)
* 2× Circular Aperture Cube (3)
* Condenser Lens Cube (4)
* Sample Cube (5)
* Objective Lens Cube (6)
* Objective in Z-Stage Cube (7)
* Eyepiece Lens Cube (8)
* 4× Screen Cube - 1× with white paper, 3× with lens tissue (9)

<p align="center">

</p>
2. Start by placing the sample - we will build the microscope around it.
<p align="center">

</p>
3. Place the Primary Image Plane (PIP) by definition: the distance is 200 mm from sample to PIP when using the 4× objective (finite-corrected for 160 mm, 40 mm working distance). Use the Sample cube with white paper as a screen.
<p align="center">


</p>

4. Place the objective lens. It is a single plano-convex lens with *f'* = 35 mm.  
<p align="center">

</p>

5. Use direct illumination from the flashlight with! its lens. Adjust the position of the objective lens - focus the image on PIP by moving the lens back or forth.

* **Focussing Trick:** Firstly move the whole objective lens cube in one direction (away from the sample). If the image sharpness in PIP improves, slide the insert in that direction. If the image sharpness in PIP get worse, slide the insert in the opposite direction, towards the sample. Continue until you get a focussed image of your sample on the PIP.

<p align="center">

</p>

6. Place the eyepiece lens behind the PIP. It is a single plano-convex lens with *f'* = 40 mm. Exchange the PIP screen with a semitransparent screen (lens tissue). While looking through the eyepiece, focus it on the PIP. Use the Focussing Trick again. The position within the cube of the sample holder for the paper screen and for the semitransparent screen has to be identical.
<p align="center">



</p>
7. Take away the screen from PIP. To dim the flashlight, put a piece of lens tissue in front of it. Look through the eyepiece - you should see a sharp image of your sample.  
<p align="center">


</p>
8. Place the Field Diaphragm (FD). The position was chosen in order to work well with the availible lenss.
<p align="center">

</p>

9. Place the condenser lens. It is a single plano-convex lens with *f'* = 40 mm.  
<p align="center">

</p>
10. Place the PIP screen back to its position.  
<p align="center">

</p>
11. Place the flashlight on one end of the baseplate.  Close the FD.
<p align="center">

</p>
12. Adjust the position of the condenser lens - focus the image of the FD on PIP by moving the lens back or forth (Focussing Trick). Once you see a sharp image of the closed FD on the screen in PIP, open and close the aperture and observe its effect.
<p align="center">

</p>
13. Remove the screen, look throught the eyepiece and check whether you see a sharp image of the closed FD.
<p align="center">

</p>

14. Place the Aperture Diaphragm (AD) into the Front Focal Plane (FFP) of the condenser lens (40 mm).

* **Focal Plane Trick** - In case you don't know where exactly the FFP is, use this:
* Use the Laser Cube with Beam Expander Cube to produce a collimated beam. Place the condenser lens in the collimated beam and find focus.
<p align="center">

</p>

* Place the AD into the same plane - slide in within the cube. Careful - push the Aperture from one side to keep it together.

<p align="center">


</p>
<p align="center">

</p>

15. Remove the lens of the flashlight. The position of the flashlight remains.
<p align="center">

</p>

16. Place the collector lens. It is a single plano-convex lens with *f'* = 50 mm.
<p align="center">

</p>
17. Remove the FD. Close the AD. Center the flashlight with respect to the AD. Focus the image of the LED on the AD by adjusting the position of the collector lens (Focussing Trick).
<p align="center">

</p>
18. Place the FD back in the illumination path. Now the Köhler illumination is properly aligned.
<p align="center">

</p>
19. Place a semitransparent screen into the Back Focal Plane (BFP) of the objective lens. Close the AD and check that you see a focussed image of the AD in the BFP.
<p align="center">


</p>
20. Remove all screens. Use a lens tissue to dim the light and look through the eyepiece. Observe the effect of opening and closing the apertures.
<p align="center">

</p>

* Left: both apertures open. Middle: FD closed. Right: AD closed.

<p align="center">



</p>

21. Exhange objective lens with 4× objective in Z-Stage. Place a screen in PIP and observe the effect of opening and closing the apertures in the PIP.
<p align="center">

</p>

* Top: both apertures open. Middle: AD closed. Bottom: FD closed.
<p align="center">



</p>

22. Remove the screen. **This is an aligned finite-corrected microscope with Köhler illumination**.
<p align="center">

</p>

23. By adding 4 more cubes and another baseplate, we will now create the **Abbe Diffraction Experiment**. The extra cubes are:

* Beamsplitter Cube (1)
* Mirror 45° Cube (2)
* Eyepiece Lens Cube (different *f'* than the previously used one!) (3)
* Relay Lens Cube (4)

<p align="center">

</p>
24. Remove the eyepiece (40 mm) and add the 4×2 baseplate. Exchange the 4× objective with the objective lens (35 mm).
<p align="center">

</p>
25. Place the Beamsplitter Cube.
<p align="center">

</p>

26. Place the screen into the PIP, in front of the Beamsplitter. Place a new eyepiece lens behind the Beamsplitter. It is a single plano-convex lens with *f'* = 100 mm. While looking through the eyepiece, focus it on the PIP (Focussing Trick).
<p align="center">

</p>
27. In the other arm we will observe the BFP. There are two options, depending on how you place the Mirror in the next step.

* Option 1: Place the mirror as shown in the picture.
* Place the eyepiece lens (40 mm).

<p align="center">


</p>

* Option 2: Place the mirror as shown in the picture.
* Place the baseplate connector on the mirror cube.
* Place the eyepiece cube (40 mm) on the connector on the mirror cube.

<p align="center">



</p>

28. Place the relay lens after the Beamsplitter. It is a single plano-convex lens with *f'* = 75 mm.
<p align="center">

</p>
29. Place a semitransparent screen in the BFP of the objective lens. Close AD and look through the eyepiece of the side arm. You should see a sharp image of the AD on the BFP.
<p align="center">

</p>

30. **This is the Abbe Difraction Experiment**. Through the eyepieces you can see both sets of conjugate planes at the same time.
<p align="center">

</p>

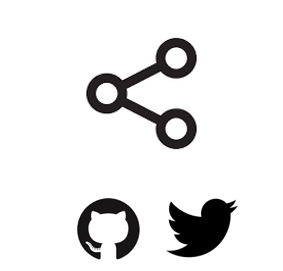
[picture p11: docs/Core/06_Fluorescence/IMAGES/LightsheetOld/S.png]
##  Participate
If you have a cool idea, please don't hesitate to write us a line, we are happy to incorporate it in our design to make it even better.

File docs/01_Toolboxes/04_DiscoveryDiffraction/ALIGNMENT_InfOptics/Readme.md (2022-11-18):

# CourseBOX: Light Microscopy and Optical Alignment (Infinity Optics)
This is the alignment procedure of the experiments with infinity-corrected optics. If you are looking for the finite-corrected setups [click here](../ALIGNMENT_FinOptics), but this page is more complex and up-to-date.  

It is more than just an alignment guide - we will also tell you about the observed effects! The explanations are marked with a :star:

Find out how to build the CourseBOX in the [BUILD_ME folder](../BUILD_ME) and try the experiments yourself.

Here you find the guidelines to show these experiments:
<p align="center">

</p>

:star: Why to switch from finite optics to infinity optics? Infinity imaging systems are much more flexible and practical than finite-corrected systems. Probably the biggest advantage of an infinity system is that you can add filters, beamsplitters and other components (but not lenses!) in the optical path without shifting the position of the image.

## First experiment: Compound Microscope and Illumination of the Sample

<p align="center">

</p>

This experiment demonstrates the essential parts of a transmission light microscope and explains the concept of conjugate planes. We will start with a simple direct illumination and build up to a proper Köhler illumination, while observing the advantages and disadvantages of each illumination type.  
<p align="center">

</p>
We will add a Beamsplitter and a side arm to split the light path in order to observe the Back Focal Plane of the objective (BFP) and the Sample / Primary Image Plane in parallel.
<p align="center">

</p>

## Second experiment: Abbe Diffraction Experiment

<p align="center">

</p>

**[Click here](https://youtu.be/NrkINpx6IMo) to watch a video of the UC2 Abbe Experiment on our YouTube channel!**  
The famous Abbe Diffraction Experiments shows how diffraction of light by a specimen (and interference with the illuminating light) creates an image and how collection of diffracted light defines the resolution of the microscope. With this setup it is possible to view both sets of conjugate planes at the same time, on a camera or a screen.
<p align="center">

</p>

We provide different apertures that can be placed in the BFP.
We use a very fine fish net as a sample here. You could try a net like [this one](https://www.amazon.de/-/en/Rryilong-Artemia-Portable-Fishing-Density/dp/B07PFNZVVS/ref=pd_vtp_199_5/261-3025835-8442122?_encoding=UTF8&pd_rd_i=B07PFNZVVS&pd_rd_r=bb7a3e28-77d9-45d8-a02c-da70409a7ff0&pd_rd_w=gHsKv&pd_rd_wg=Ojv0t&pf_rd_p=80911889-e795-4970-aa72-4c8dbf7a55d0&pf_rd_r=2SB3XXENVTP7HBN5MD5Q&psc=1&refRID=2SB3XXENVTP7HBN5MD5Q). Another idea is to try one of these plastic [tea bags](https://www.jenierteas.com/kaika-cherry-sencha-green-tea-pyramid-tea-bags-p1120/). Or of course you can take a proper diffraction grating (but where's the fun in that?). If you have other ideas for cool samples, let us know!

[Skip to the Abbe Diffraction Experiment](#abbe-diffraction-experiment)

##  This tutorial will lead you step-by-step through the alignment of the Compound Microscope, different Illumination types and the Abbe Diffraction Experiment and explain the optical phenomena you observe with these systems

1. Start with five 4×1 baseplates mounted as shown in the picture to an optical breadboard or to a wooden board. Prepare the following cubes:

* Sample Cube (1)
* Flashlight Cube (2) - Use the flashlight WITHOUT its lens in all the experiments
* 2× Circular Aperture Cube (3)
* Screen - Sample Holder Cube with white paper (4)
* 5× Lens Cube with 50 mm lens (5)
* 3× Lens Cube with 100 mm lens (6)
* Eye Cube (7)
* Beamsplitter Cube (8)
* Raspi Camera Cube (9)

Also prepare:

* Raspberry Pi
* UC2 Alignment Tool
<p align="center">

</p>

:star: Why to use the flashlight without the lens? It would be one too many lenses in out system. In order to image the LED with our illumination optical path, we need to have access to the bare LED. Before you start building the microscope, remove the lens from the  flashlight.
<p align="center">


</p>

### :star: Infinite conjugate imaging system
We form a real image of the sample by a method known as infinite conjugate system. If the object is placed in the focal plane of a lens, its image is formed in the infinity, because the rays diffracted by the object are parallel after the lens. If a second lens is placed after the first one, it captures these parallel rays and a real image of the object is formed in the focal plane of the second lens. The magnification of an infinite conjugate system is given by  
***M = -f<sub>2</sub>/f<sub>1</sub>***

2. Start by placing the sample - we will build the microscope around it.
<p align="center">

</p>

* **Alignment trick:** Use the Alignment Tool and align all inserts (Sample, screen, lenses) to the centers of the cubes as you place them on the baseplate. This ways, because we use 50 mm and 100 m lenses, you will have the whole setup roughly pre-aligned from the beginning.
<p align="center">

</p>

3. Place the objective lens. It is a single plano-convex lens with *f'* = 50 mm.
<p align="center">

</p>

### :star: Numerical Aperture and Resolution
The Numerical Aperture (NA) describes how much light coming from an imaged object is captured and focussed by the objective and determines the resolution of the system (and not just that). It is given by  
***NA = n × sin(alpha)*** ,  
where *n* is the refractive index of the medium between the sample and the objective (here, in air, *n* = 1) and *alpha* is the angle of the between the optical axis and the steepest rays that are still collected by the objective. The angle *alpha* can be calculated from the focal length *f'* of the objective lens and its diameter *d*, because  
***tan(alpha) = 1/2 d / f'*** .  

<p align="center">

</p>

From the NA we can calculate the resolution of our imaging system. Physically, the resolution s the smallest distance between two point is the sample that are still imaged as two point. If the points are any closer, the will appear as a single point in the Image Plane. For the microscope here, we calculate the resolution as  
***R = 0,61 lambda / NA*** ,  
where *lambda* is the wavelength of the illumination. Because we use a white light source, we take *lambda* = 550 nm, since this is roughly in the middle of the visible spectrum.

4. Place the tube lens. It is a single plano-convex lens with *f'* = 100 mm.  
<p align="center">

</p>

5. Place the Primary Image Plane (PIP) in the focal plane of the tube lens. Use the Sample cube with white paper as a screen.
<p align="center">

</p>

:star: Now we have the imaging infinite conjugate system. The second lens can be placed at any distance from the first one, because the rays are parallel after the first lens. As long as the system is well aligned, the distance between the lenses doesn't really matter. Of course it shouldn't be across the whole room, because we would loose intensity and some of the marginal rays. Here we build it in such a way that the Back Focal Plane of the Objective coincides with the front focal plane of the tube lens, which is the most optimal way for Fourier imaging and it will be convenient for the next steps.

:star: Numerical aperture of our imaging system equals to *NA = 1 × sin(alpha)* , with *alpha* coming from *tan(alpha) = 0,5×25,4 / 50*. Therefore our *NA* = 0,25.  The resolution of our microscope is then *R = 0,61×0,550 / 0,25 = 1,342 um* .  

### :star: Direct Illumination
To start with the simplest way of illuminating a sample, we  place the flashlight, our light source, close to the sample. This way we can see an image of our sample on the screen. This is called Direct illumination, but it's a very inefficient illumination type because  only a small fraction of the light emitted from the source will actually hit the sample.
<p align="center">

</p>

6. *Starting with Direct illumination:* Use the flashlight WITHOUT its lens as a direct illumination source, its exact position is not that important. The Sample has to be in the front focal plane of the objective and the screen has to be in the back focal plane of the tube lens - you can use the I. Focussing Trick. Adjust the position of the inserts to focus the image on PIP - you can use the II. Focussing Trick.
<p align="center">


</p>

* **Focussing Trick I for infinity optics:** How to make sure that a screen (sample, aperture) is in the focal plane of a lens? Place the Lens cube and the paper screen on a baseplate in roughly the aligned distance (depending on the focal length of the lens). Image something from the infinity on the screen with this lens. A good object in the infinity can be the clouds in the sky or a window on the other side of the room (at least 4-5 m away). Shift the Insert carrying your screen inside the cube to see a sharp image of the clouds/window/... Now you know the distance in which you want to have the component that is supposed to be adjacent to the lens.
* **Focussing Trick II for general alignment:** Firstly move the whole Sample cube with the screen in one direction (away from the tube lens). If the image sharpness in PIP improves, slide the insert in that direction. If the image sharpness in PIP gets worse, slide the insert in the opposite direction, towards the sample. Continue until you get a focussed image of your sample on the PIP.
* **Alignment Check:** When your imaging path is properly aligned, the distance between the objective and the tube lens doesn't matter, because the light rays between the lenses are parallel to the optical axis. Check this by moving the Tube lens and screen TOGETHER forwards or backwards by a baseplate-unit or two. The image on the screen must not change.  
:star: Now you can see that we were right about the infinite conjugate system.
<p align="center">

</p>

:star: The magnification of an infinite conjugate system is given by *M = - f<sub>2</sub>/f<sub>1</sub>* as we said. In infinity-corrected microscopes it is usually described as *M = - f<sub>Tube lens</sub>/f<sub>Objective</sub>* for the imaging system. The magnification of our imaging system here is therefore *M =* - 100/50 = -2. We can see an inverted 2× magnified image of our Sample in the Primary Image Plane.

### :star: Critical Illumination
To capture all the light from the flashlight, we build a second infinite conjugate system on the illumination side of the sample. This will form an image of the flashlight's LED on the sample. This is called critical illumination. The advantage of having an infinite conjugate critical illumination is that we can include an Aperture diaphragm (AD). The AD limits the range of angles of the rays that illuminate the sample and therefore influences the resolution and contrast.
<p align="center">

</p>

7. *Building Critical illumination:* Move the flashlight further from the Sample as shown in the picture.
<p align="center">

</p>

8. Place a collector lens next to the flashlight. It is a single plano-convex lens with *f'* = 50 mm.
<p align="center">

</p>

9. Place the condenser lens in front of the Sample. It is a single plano-convex lens with *f'* = 50 mm.  
<p align="center">

</p>

10. Place the Aperture Diaphragm (AD) between the collector and condenser. You can roughly align it to the center of the cube and precisely align it with the lenses using I. Focussing Trick. This is a microscope with critical illumination.  
<p align="center">

</p>

11. Let's have a look at the effect of the AD. You should be able to see it on the Sample itself but here we placed the paper screen in the position of the sample to be able to picture it.  
The LED of the flashlight is now imaged directly on our sample. The flashlight used here is extremely bright and therefore the pictures shown here might look a bit misleading, because it wasn't possible to take a better, not oversaturated pictures.  
:star: Both the collector and condenser lens have focal length of 50 mm, therefore the magnification of this infinite conjugate system is equal to -1. We see an image of the LED, in real size but inverted, on the sample.   
Top left: AD open, the spot is very bright.  
Top right: AD closed, the spot seems smaller but it's just less bright. We can recognize the shape of the LED imaged in this plane.  
Bottom: In PIP, we seen the image of the LED over the image of the Sample.  
:star: The magnification of multiple infinite conjugate systems in a row is given by their multiplication. The image of the LED that we see in the PIP is given by *M<sub>LED in PIP</sub> = M<sub>Illumination</sub>×M<sub>Imaging</sub> =* -1 × -2 = 2. We can see a non-inverted 2× magnified image of the LED in the Primary Image Plane.

<p align="center">



</p>

### :star: Köhler Illumination
With the critical illumination, the sample is not illuminated uniformly and in case of a very bright light source, like here, the image of the source is more visible than the image of our sample. We can solve this by adding one more lens to the illumination system, so that the image of the LED is formed on the AD instead of the sample. This way the illumination of the sample is uniform. Furthermore, we can add another diaphragm, known as the Field diaphragm (FD). The FD is imaged on the sample and allows for limiting the illuminated area.  
This illumination technique is called the Köhler Illumination and it is the most common one for light microscopy.  
The goals of illumination in microscopy are:
* illuminate the specimen uniformly over an adjustable area
* illuminate the objective aperture uniformly over an adjustable angle

and Köhler Illumination gives us both.
<p align="center">

</p>

12. *Upgrading to Köhler illumination:* Move the flashlight further from the critical illumination as shown in the picture. Keep the critical illumination part as it was.
<p align="center">

</p>

13. Place a new collector lens next to the flashlight. It is again a single plano-convex lens with *f'* = 50 mm.
<p align="center">

</p>

14. Place the Field Diaphragm (FD) between the new collector and old collector. You can roughly align it to the center of the cube and precisely align it with the lenses using I. Focussing Trick. This is a microscope with Köhler illumination.  
:star: Why do we need to illuminate the specimen uniformly over an adjustable area? Large area of object illuminated provides large disc of light at primary image causing reflections from walls of microscope and reduction in contrast. We adjust the illuminated area with the FD.

<p align="center">

</p>

15. In the Köhler illumination, the aperture closer to the light source s the Field diaphragm (FD) and the one closer to the sample is the Aperture diaphragm (AD).  
:star: Why do we need to illuminate the objective aperture uniformly over an adjustable angle? If the illuminating aperture is too small, resolution will be reduced and image quality will be impaired though contrast will be increased. If the illuminating aperture is too large, light will be scattered from the edges of the objective lens, thus reducing contrast. For the best resolution, the illuminating aperture should be 60%-75% of the imaging aperture. We adjust the illuminating aperture with the AD.

<p align="center">

</p>

16. In the Köhler illumination, the first lens after the light source is called the Collector lens. The lens between the apertures is called a Field lens. The one in front of the Sample is again the condenser lens, just as in the critical illumination.  
:star: Thanks to this configuration of three lenses, the LED is imaged on the AD and the FD is imaged on the Sample.

<p align="center">

</p>

17. Let's have a look at the effects of the apertures in the Sample plane. Note: because the LED is very strong, the effect of the AD is not so apparent.  
:star: In the Sample Plane: The FD is imaged on the Sample. It limits the size of the illuminated area and we can directly see the image of the FD when we close it. The AD limits the parallel light beam between the Field lens and the Condenser lens. It limits the illumination angles and therefore changes the intensity of the illumination.   
Top left: both apertures open.  
Top right: FD closed, AD open.  
Bottom left: FD open, AD closed.  
Bottom right: both apertures closed.  

<p align="center">




</p>

18. Let's have a look at the effects of the apertures in the Primary Image Plane. Note: because the LED is very strong, the effect of the AD is not so apparent.  
:star: In the Primary Image Plane: The FD and AD have the same effect as in the Sample Plane.   
Top left: both apertures open.  
Top right: FD closed, AD open.    
Bottom left: FD open, AD closed.  
Bottom right: both apertures closed.  

<p align="center">




</p>

19. Remove the screen from PIP.
<p align="center">

</p>

### :star: Eyepiece
So far we could consider our microscope a simple one, because the image is magnified by only one system of lenses (Objective and a Tube lens together). A compound microscope uses two systems of lenses - objective and eyepiece, that multiplies (compounds) the objective. This way we can achieve higher magnification.  
The magnification of an eyepiece is given by  
***M = 250 mm/f<sub>Eyepiece</sub>*** ,     
where 250 mm is an estimate of the "near point" distance of the eye - the closest distance at which the healthy naked eye can focus without too much strain.  
The eyepiece images the PIP to the infinity, making it observable by the naked eye.
<p align="center">

</p>

20. Place an eyepiece lens behind the PIP position. It is a single plano-convex lens with *f'* = 50 mm.
<p align="center">

</p>

21. **Careful!** Put a lens tissue in front of the flashlight to dim it before you look into the strong light. Then look through the eyepiece lens. Note: because the LED is very strong, the effect of the AD is not so apparent.  
:star: With the eyepiece we observe the Sample Plane imaged on the PIP. The diaphragms will have the same effect as we observed in the previous steps.    
Top left: both apertures open.  
Top right: FD closed, AD open. Here we see the issue caused by the super bright light source - we should see the image only in the very bright region and not around it.  
Bottom left: FD open, AD closed.  
Bottom right: both apertures closed. Here we see the issue caused by the super bright light source - we should see the image only in the very bright region and not around it.

<p align="center">




</p>

:star: Note that you cannot put your eye anywhere behind the eyepiece. To maximize the field of view, your iris (the pupil of the eye) must match the so-called Ramsden disc. This is the smallest diameter of the light beam coming from the eyepiece. You can find it using a piece of paper and tracing the Light that emerges from the eyepiece. The smallest spot is roughly in the focal plane of the eyepiece (If your microscope is properly aligned).

22. Place the Eye Cube behind the eyepiece. On the back of the "Eye" you can see the image similarly as it's formed on your retina.
<p align="center">


</p>

23. **This is an aligned compound infinity-corrected microscope with proper Köhler illumination**.
<p align="center">

</p>

24. Place the RasPi Camera in the PIP and switch on the UC2-GUI on the RasPi. The field of view of the camera is much smaller than the one of the eye or with the paper screen. Align the camera to see a sharp image (II. Focussing Trick).
<p align="center">

</p>

### :star: Field set and Aperture set of conjugate planes
In any imaging system there are two important sets of planes: Field set, containing the images of the object and the Field diaphragm and Aperture set, containing the images of the light source and the Aperture diaphragm. Those two sets are mathematically related to each other by Fourier transform. Both sets therefore contain all the information of the image and the image can be manipulated in either of them.  
In order to observe both sets of planes simultaneously, we can build a side arm and image the BFP there.  
The Aperture set of conjugate planes: Lamp filament, Aperture diaphragm, Back Focal Plane of the objective, Exit pupil of the eye. The BFP will be imaged in the side arm.
<p align="center">

</p>
The Field set of conjugate planes: Field diaphragm, Sample plane, Primary Image Plane, Retina. The BFP will be imaged in the side arm while the image of the sample can be observed in the main arm.
<p align="center">

</p>

Because we've build our system entirely of infinite conjugates, each pair of lenses is imaging whatever is in the front focal plan of the first one in the back focal plane of the second one. Thanks to this, we have access to all the conjugate planes and we can easily manipulate them.

25. *Building the side arm:* Place the Beamsplitter Cube. It has to be oriented in such a way that it will reflect half of the incoming light in the direction of the side arm. The rest of the incoming light is still transmitted to the PIP.
<p align="center">

</p>

26. Place the first relay lens next to the Beamsplitter, in the side arm. It is a single plano-convex lens with *f'* = 100 mm.
<p align="center">

</p>

27. Place the second relay lens behind the first one, in the side arm. It is also a single plano-convex lens with *f'* = 100 mm.
<p align="center">

</p>

:star: We build another infinite conjugate system in the side arm and its magnification is again given by *M = - f<sub>2</sub>/f<sub>1</sub>* . Because both of the relay lenses have the same focal length (100 mm), the magnification in the side arm is equal to -1. We can see an inverted image of the BFP, in the same size as in the actual Back Focal Plane of the Objective.

28. Place the paper screen in the focal plane of the second relay lens. This is where you image the back focal plane of your objective.
<p align="center">

</p>

29. Let's have a look in the BFP, as it's imaged in the side arm.  
:star: In the BFP the apertures have the opposite effect as in the PIP. The AD is imaged into this plane while the FD limits the angles of the illuminating rays. We also see an image of the LED in the BFP.  
Top left: both apertures open.  
Top right: FD closed, AD open. The image is dimmer.     
Bottom left: FD open, AD closed. The illuminated area is smaller.  
Bottom right: both apertures closed.

<p align="center">




</p>

30. Switch the camera with the paper screen, so we can see the BFP on the RasPi. We could see the Fourier transform of our cat there but because of the high intensity of the flashlight, we only see the image of the LED.  
:star: The magnification of the LED image formed here is given by the multiplication of the magnifications of al the infinite conjugate systems that are imaging it. It is given by *M<sub>LED in BFP</sub> = - f<sub>Field lens</sub>/f<sub>Collector</sub> × f<sub>Objective</sub>/f<sub>Condenser</sub> × f<sub>Relay lens 2</sub>/f<sub>Relay lens 1</sub>* . Because each pair of the lenses has actually the same focal length, the magnification of the LED in the BFP is -1 and we see an inverted non-magnified image of it.

<p align="center">

</p>

31. **This is the complete first experiment: Compound Microscope with Köhler Illumination and access to all the conjugate planes.**  You would be able to demonstrate the Abbe Diffraction Experiment with this as well but it's much nicer with the setup we will build now.
<p align="center">

</p>

## Abbe Diffraction experiment

### :star: Abbe Diffraction experiment
Until Ernst Abbe and Carl Zeiss teamed up in 1866, microscopes were produced by the trial and error method. Abbe discovered after many calculations and experiments that the diffraction image in the Back Focal Plane of the objective is essential for image formation. We're going to explain his findings during the demonstration of his famous experiment.   
We use a laser pointer as a light source and expand it using two lenses. The imaging path is the same as in the microscope in the first experiment and therefore we can observe the image of our sample in the main arm and the image of the BFP in the side arm.
<p align="center">

</p>

32. We use a very fine fish net as a sample here. You could try a net like [this one](https://www.amazon.de/-/en/Rryilong-Artemia-Portable-Fishing-Density/dp/B07PFNZVVS/ref=pd_vtp_199_5/261-3025835-8442122?_encoding=UTF8&pd_rd_i=B07PFNZVVS&pd_rd_r=bb7a3e28-77d9-45d8-a02c-da70409a7ff0&pd_rd_w=gHsKv&pd_rd_wg=Ojv0t&pf_rd_p=80911889-e795-4970-aa72-4c8dbf7a55d0&pf_rd_r=2SB3XXENVTP7HBN5MD5Q&psc=1&refRID=2SB3XXENVTP7HBN5MD5Q). Another idea is to try one of these plastic [tea bags](https://www.jenierteas.com/kaika-cherry-sencha-green-tea-pyramid-tea-bags-p1120/). Or a diffraction grating.
<p align="center">

</p>
33. We provide a circular aperture and a rectangular aperture to be used in the BFP. We also suggest to use an opaque dot (a small dot made with some marker or pain on a microscope slide) and a thin line object (like this tiny hex key here). The apertures block the light from the outside while the dot and line can block the center of the light path.
<p align="center">





</p>
34. As mentioned earlier, we keep the imaging path in both main arm and side arm. Remove the illumination part of the microscope and also the Eyepiece.
<p align="center">

</p>

35. Besides the apertures that we already prepared, we will need :

* Laser Cube with laser pointer (1)
* 1× Lens Cube with 50 mm lens (2)

For now, place the camera in PIP.  
<p align="center">

</p>

36. The laser is equipped with a cap that holds a lens from the RasPi camera. Make sure to put it on, otherwise you won't be able to create an expanded parallel beam.  
<p align="center">


</p>
37. Place the Laser cube on the baseplate as shown in the picture.

**Careful!** Do not hit anybody's eyes with the laser beam. Keep the laser off if you're not using it at the moment. Always point the laser away from people. Block the light if it's leaving the table you're working on.

<p align="center">

</p>

38. Place the lens for beam expansion behind the Laser cube as shown in the picture. It is a single plano-convex lens with *f'* = 50 mm. Align the lens to illuminate your Sample with a collimated beam - the diameter of the beam should be the same just after the lens cube and also far away from it. When you beam is well-collimated, the distance between the laser+lens duo and the Sample doesn't matter.
<p align="center">


</p>
39. You can switch the camera between the PIP and the BFP. You could also use two cameras, one in PIP and one in BFP, if you have them.
<p align="center">

</p>
40. Between the objective and the Beamsplitter is the Back Focal Plane of the Objective. You can see it if you put a piece of paper there - you will see the Fourier transform of the sample. You should see the same on  camera in the side arm.
<p align="center">

</p>

41. In the PIP, you can see an image of the sample. Here we see our fish net. Align the camera to obtain a sharp image.  
:star: Because of the [Talbot effect](https://en.wikipedia.org/wiki/Talbot_effect) you can find more than one sharp image of the sample. Therefore, partially close the Field diaphragm (FD) and find the position of the camera where you not only see a sharp image of the grating (fish net) but also of the FD.

<p align="center">

</p>

42. In the BFP image in the side arm, you can see the Fourier transform of the grating just as it looks in the BFP itself. Align the second Relay lens to obtain a focussed image on the camera.  
:star: The grating is regular in both X and Y and therefore it's a very convenient sample for this experiment, because its Fourier transform is easily predictable. With a different sample the BFP will of course also look differently.

<p align="center">

</p>

### :star: Back Focal Plane
The intensity peaks in the BFP are the diffraction orders of our sample. By placing an aperture or another object here we’ll be able to modify the information transmitted through the microscope that contributes to the image. Depending on the aperture we can observe different effects.

* *Circular aperture:* The circular aperture blocks the light symmetrically from outside towards the center. Close the aperture and align the laser such that the 0<sup>th</sup> order is in the center of the aperture. You can align the laser using the four screws in its holder.
<p align="center">


</p>

* *Rectangular aperture:* The rectangular aperture closes independently from both sides in X and Y direction (horizontally and vertically). Use a hex key or a similar tool to close/open the aperture doors.
<p align="center">


</p>

* *Dot and line:* Use a sample holder cube or your (presumably steady) hand to hold these two. You can block the 0<sup>th</sup> or 0<sup>th</sup>+1<sup>st</sup> orders with the dot, depending on how big it is. You can block the X-0<sup>th</sup> or Y-0<sup>th</sup> order with the line-object.
<p align="center">


</p>

43. **This is the setup for the second experiment: Abbe Diffraction Experiment.**
<p align="center">

</p>

## :star: Abbe Diffraction experiment - What do we see?
1. With no aperture in the BFP, we see the image of the Sample in PIP and the Fourier transorm of the sample in the BFP, as we just aligned it and prepared it.
<p align="center">

</p>
1. Firstly we use the Circular aperture. As we slowly close it and change the diameter of the transmitting area, we cut out the higher diffraction orders that carry the high frequency information, hence the fine details. In the image plane we see how these details blur and the sharp edges soften. The more orders we cut out, the blurrier the image gets.
<p align="center">

</p>
1. Using the Rectangular aperture, we can block the diffraction orders more selectively. When we close the aperture in the X direction to only let through the Y-0<sup>th</sup> orders, the square pattern of the image disappears, and we have only lines. This is because there is no X order that would transmit the information about the shape in the perpendicular direction.
<p align="center">

</p>
1. When we do the same trick in the other direction, we then see lines of the other orientation but again no square pattern.
<p align="center">

</p>
1. Closing the aperture in both X and Y direction, we eventually block all the higher orders that form the image of the sample. As we can see here, when only the 0<sup>th</sup> order is transmitted all image information is lost. What we see is only some background noise.
<p align="center">

</p>
1. On the other hand, when we block only the 0<sup>th</sup> order but keep all the others (we do this using the dot on a slide), we are still able to see the pattern is preserved, because all the orders still have a corresponding partner to interfere with on the other side from the 0<sup>th</sup> order. But now we are in a so-called dark field imaging mode. We'll explain it in the next steps.
<p align="center">

</p>
1. We can even block the 0<sup>th</sup> and 1<sup>st</sup> order by simply using a bigger dot in the BFP. We are still able to recognize the square pattern but the high frequency information, the noise, is taking over the image.
<p align="center">

</p>
1. When using the line object instead of the dot, we can block the 0<sup>th</sup> order completely in the Y direction and see what it does to the image. We still see the square pattern but suddenly, in the X direction, it seems that we have twice as many squares. This is the dark field imaging effect but in X only. We’re seeing just the edges and because there are two edges per square in one direction, it appears that we see them twice.
<p align="center">

</p>
1. The same works also in the perpendicular direction - blocking the 0<sup>th</sup> order in X results in the dark field imaging mode in Y.
<p align="center">

</p>
1. Using the rectangular aperture again and we can find out what is the minimal amount of orders that we need to form a reliable image. We said that they always interfere with the 0<sup>th</sup> order, so we don't need both sides. Therefore, we close the aperture and let through only one quarter of the orders. We can block the higher orders as well, as they only carry the high frequency information, and we are still able to see the basic pattern of our sample.  
<p align="center">

</p>

## :star: Watch the video of this experiment!
 UC2 YouSeeToo - Abbe Experiment Demonstration (https://youtu.be/NrkINpx6IMo)

Notes to the video:
* In this demonstration of the experiment, two Alvium cameras from Allied vision are used, so we can show the PIP and BFP on the screen simultaneously
  * Find the cubes for the Alvium cameras [here](../../../CAD/ASSEMBLY_CUBE_AlliedVision_Alvium) anch choose the adjustable insert for easy alignment.
* The optical path is different from the one described in this tutorial. This is because of the use of the above mentioned cameras
  * The objective and eyepiece are both lenses with *f'* = 100 mm. The magnification of the microscope is therefore equal to 1. The "magnified" image is just a zoom into the camera view.
  * Thanks to the use of a 10 mm lens as an objective, the diffraction orders in BFP are more separated and easily accessible.
  * In the side arm, the first lens has *f'* = 100 mm and the second lens *f'* = 50 mm. The image of the BFP is therefore demagnified twice, to fit better in the field of view of the camera.

**Bonus question:** This magical image was taken by the RasPi camera in the BFP with the fish net as a sample. If you tell me what created this effect, I send you a chocolate ;-)
<p align="center">

</p>

##  Participate
If you have a cool idea, please don't hesitate to write us a line, we are happy to incorporate it in our design to make it even better.

#### References:
[1](https://www.biodip.de/fileadmin/user_upload/Documents/Resources/Teaching_materials/theory_pdfs/03_Conjugate-Planes.pdf);  [2](https://www.wikilectures.eu/w/Abbe%E2%80%99s_theory);  [3](https://www.microscopeworld.com/p-3470-what-is-a-compound-microscope.aspx);  [Cat image source](https://www.facebook.com/TheOfficialGrumpyCat/);   
4 Advanced Optical Imaging Workshop; Plymouth; Noah Russell, 2009©

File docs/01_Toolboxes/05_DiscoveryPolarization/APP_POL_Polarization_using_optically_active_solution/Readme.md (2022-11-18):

# Polarization Experiment using Optically Active Solution

<p align="center">

</p>

The optical activity was discovered by Arago in the quartz in 1811. In 1847, molecular chirality was observed by scientist Louis Pasteur. He found that natural tartaric acid is optically active, and its external crystals have isomerism and chiral morphology *[1]*.

Two molecules with the same chemical formula, the mirror image of the other, describe molecular chirality. These come in two varieties: dextrorotatory (rotate plane-polarized light clockwise) and levorotatory (counterclockwise).

Sucrose is a disaccharide made of glucose and fructose and dextrorotatory, which rotates the plane-polarized light to the right. A well-known example of sucrose is table sugar produced naturally in plants. Fructose is a simple ketonic sugar and levorotatory which rotates the plane-polarized light to the left. Glucose is a simple sugar that belongs to the carbohydrate family and is dextrorotatory. The molecules of fructose and glucose are mirror images of each other. Corn syrup is one of the most commonly used sugar solutions *[2]*.

Two simple sugar-water solutions were prepared and used in the experiment. The first solution was produced with one cup of table sugar and one cup of water. Table sugar is sucrose and dextrorotatory, turning clockwise to the right plane-polarized light. Grape sugar is dextrorotatory and glucose, and the second solution mixes grape sugar (Traubenzucker) and water components in the same amount. It rotates the incoming light polarization state to the right, clockwise direction. However, two solutions have different polarization states at the same time because of their molecular structure and demonstrate different colors inside the crossed polarizers.

<p align="center">
s
</p>

In the image, Table sugar-water solution is shown in left-side, Grape sugar-water solution is in the right glass.

## Parts

### Modules for this setup

|  Name | Properties  |  Price | Link  | # |
|---|---|---|---|---|
|  4×1 Baseplate | Skeleton of the System | 5.47 €  | [Base-plate](../../CAD/ASSEMBLY_Baseplate)  | 1 |
|  MODULE:  *Polarizer Cube* | It holds the linearly polarizing filter  |  8.62 €  | [Linear Polarizer](../../CAD/ASSEMBLY_POL_Linear_Polarizer)  | 2 |
|  MODULE:  *Active Solution Chamber* | It contains sugar-water solutions.  |  7.32 €  | [Active Solution Chambers](../../CAD/ASSEMBLY_POL_Active_Solution_Chamber)  | 1 |
|  EXTRA MODULE: Flashlight Lamp Cube | Light Source  | 7.2 €  | [Flashlight](../../CAD/ASSEMBLY_CUBE_Flashlight)  | 1 |

### Parts to print

* 1 × [Base-plate 4×1](/POLARISATION/ACTIVE/Assembly_Cube_Baseplate_4x1_v2.stl)
* 2 × [Cube base 1×1](/POLARISATION/ACTIVE/10_Cube_1x1_v2.stl)
* 2 x [Cube lid 1×1](/POLARISATION/ACTIVE/10_Lid_1x1_v2.stl)
* 2 × [Polarizer Guide](/POLARISATION/ACTIVE/20_POL_Cube_Insert_Linear_Polarizer_Guide.stl)
* 2 × [Polarizer Wheel](/POLARISATION/ACTIVE/20_POL_Cube_Insert_Linear_Polarizer_Wheel.stl)
* 2 × [Polarizer Lid](/POLARISATION/ACTIVE/20_POL_Cube_Insert_Linear_Polarizer_Lid.stl)  
* 1 × [Cube Lid 2x1](/POLARISATION/ACTIVE/10_Lid_el_2x1_v2.stl)
* 1 x [Active Solution Chamber - Alternative 1 with Two Sections](/POLARISATION/ACTIVE/10_POL_Active_Solution_Chamber_90long_40High_Double_TOP.stl)
* 1 x [Active Solution Chamber - Alternative 2 with One Sections](/POLARISATION/ACTIVE/10_POL_Active_Solution_Chamber_90long_40High_TOP.stl)    
__*Extra Holder Parts but NOT USED in our experiment:*__
* 1 × [Flashlight Holder](/POLARISATION/ACTIVE/20_Cube_Insert_Holder-okular+flashlight_v2.stl)

<p align="center">

</p>  

##  Additional components
* Check out the [RESOURCES](../../TUTORIALS/RESOURCES) for more information!
* 1 × Linear Polarizing Sheet [🢂](https://amazon.de/-/en/Polarizing-A4-Sheet-Polarizer-Educational-Polarized/dp/B06XWXRB75/ref=pd_sbs_421_3/262-2115536-7173904?_encoding=UTF8&pd_rd_i=B06XWXRB75&pd_rd_r=b88e7340-b061-4e0b-8daa-8ec533fd7c71&pd_rd_w=qlkAY&pd_rd_wg=At9EZ&pf_rd_p=a03ac387-6e4d-4f6b-96b6-1853da0bb37b&pf_rd_r=49HX2Z4Q5KRZSQ2FWRQR&psc=1&refRID=49HX2Z4Q5KRZSQ2FWRQR)
* 24 × 5 mm Ball magnets [🢂](https://www.magnetmax.de/Neodym-Kugelmagnete/Magnetkugel-Kugelmagnet-O-5-0-mm-Neodym-vernickelt-N40-haelt-400-g::158.html)
* 20 x Screws DIN912 ISO 4762 - M3×12 mm [🢂](https://eshop.wuerth.de/Zylinderschraube-mit-Innensechskant-SHR-ZYL-ISO4762-88-IS25-A2K-M3X12/00843%20%2012.sku/de/DE/EUR/)
* 6 x Screws DIN912 ISO 4762 M2×16 mm [🢂](https://www.amazon.de/Edelstahl-Sechskopf-Knopf-Schrauben-Unterlegscheiben-Sortiment-Aufbewahrung/dp/B073SS7D8J/ref=sr_1_fkmr0_1?__mk_de_DE=%C3%85M%C3%85%C5%BD%C3%95%C3%91&keywords=zylinderkopfschrauben+set+galvanisiert&qid=1565007371&s=diy&sr=1-1-fkmr0)
* 2 x metal plates
* Microscope Rectangular Coverslips [🢂](https://www.ebay.de/itm/223260964391?hash=item33fb63f627:g:pukAAOSwsGpb%7E14N)
* _NOT USED_ 1 × flashlight [🢂](https://www.pollin.de/p/led-taschenlampe-alu-5-w-cree-led-3xmicro-schwarz-b-ware-535448)

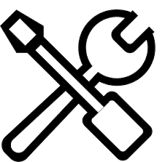
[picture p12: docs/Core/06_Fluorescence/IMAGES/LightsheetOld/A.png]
##  Assembly

* [Baseplate](../../CAD/ASSEMBLY_Baseplate)
* [Linear Polarizer Cube](../../CAD/ASSEMBLY_POL_Linear_Polarizer)  
* [Active Solution Chambers](../../CAD/ASSEMBLY_POL_Active_Solution_Chamber)  
__*EXTRA MODULE:*__
* [Flashlight cube](../../CAD/ASSEMBLY_CUBE_Flashlight)

<p align="center">

</p>  

##  Results

We printed and assembled two Linear Polarizer and Active Solution Chamber module parts. Then, we bought the necessary components and inserted them into cubes.  
You can see the datils of the Active Solution Chamber designs.

<p align="center">

</p>

<p align="center">

</p>

Two different chamber design is shown in the image below. Left-side chamber has a container only for 1 active solution. In the other one, two different mixtures can be observed in the same time.  

<p align="center">

</p>

You can find the basic version of Polarization Using Optically Active Solution experiment with an additional flashlight source below.  Depends on the experiment place conditions, you can add an extra light source.

<p align="center">

</p>

The chamber module was inserted between two linear polarizers, the Crossed Polarizers. We can observe the direct effect of the angle between two linear polarizers in the video below. The intensity of passing light through crossed polarizers changes when the direction angle of the polarization filter changes 360 degrees.

Experimental result of two optically active solutions is shown in the video:      
   *  Left Is Grape Sugar-water Solution (Glucose) Table,          
   * Right Is Sugar-water Solution (Sucrose

<p align="center">

</p>

## References

[1] Gal, J. (2017). Pasteur and the art of chirality. Nature Chemistry, 9(7), 604–605. https://doi.org/10.1038/nchem.2790    

[2] Logiurato, F. (2018). Teaching Light Polarization by Putting Art and Physics Together. The Physics Teachers, 1–5. https://arxiv.org/ftp/arxiv/papers/1803/1803.09645.pdf

## New Ideas
We are open to new ideas. Please contribute the project freely, this place is a free country which is built by codes and machines :robot:

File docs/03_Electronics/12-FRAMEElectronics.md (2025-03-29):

# FRAME Electronics Hardware

Development repository for electronic parts of the mAIkroscope (formerly fiveD/XYZ)

## Table of Contents

- [mAIkroscope-electronics-hardware](#maikroscope-electronics-hardware)
  - [Table of Contents](#table-of-contents)
  - [CANBUS as communication between devices](#canbus-as-communication-between-devices)
  - [hatplus-for-raspberrypi-5](#hatplus-for-raspberrypi-5)
    - [Raspberry Pi HAT+ implementation (EEPROMS, HAT+ spec)](#raspberry-pi-hat-implementation-eeproms-hat-spec)
    - [Raspberry Pi pinout](#raspberry-pi-pinout)
    - [ESP32 pinout](#esp32-pinout)
    - [Emergency STOP connector](#emergency-stop-connector)
    - [HAT: Terminating CANBUS or activating CAN activity indicator LED](#hat-terminating-canbus-or-activating-can-activity-indicator-led)
    - [Disabling communication or power-switching functions](#disabling-communication-or-power-switching-functions)
  - [stepper-backpack](#stepper-backpack)
    - [Pinout](#pinout)
    - [Current sensing and current setting](#current-sensing-and-current-setting)
    - [Converting Rev. C from 12V+CAN to 5V+I2C](#converting-rev-c-from-12vcan-to-5vi2c)
    - [Terminating CANBUS or activating CAN activity indicator LED](#terminating-canbus-or-activating-can-activity-indicator-led)
  - [Laser-interface](#laser-interface)
    - [XIAO pinout](#xiao-pinout)
    - [Keyswitch specifications and connections](#keyswitch-specifications-and-connections)
    - [Interlock](#interlock)
      - [Interlock behavior and status inticators](#interlock-behavior-and-status-inticators)
      - [Interlock sources](#interlock-sources)
      - [Interlock overrides](#interlock-overrides)
    - [Solderjumpers](#solderjumpers)
    - [Using the board as CAN-to-GPIO converter](#using-the-board-as-can-to-gpio-converter)
  - [Pogopin-connectors](#pogopin-connectors)

## CANBUS as communication between devices

CANBUS is a differential bus where many devices are connected to the same CAN_H and CAN_L wires, then can communicate with each other.

The electrical functionality requires a dedicated CAN transceiver chip for every device connecting to the bus. The receiver converts differential signaling on the bus to input and output interfaces, while providing tolerance to voltages of commonly 20V on the CAN_H/CAN-L and isolating faulty voltages from reaching to the GPIOs of connected controllers.

The two wires of CANBUS need to be connected together with two 120 Ohm resistors at opposite ends. This termination is like impedance matching and prevents the signals to reflect back from a far end of the bus wires. The terminators should be placed on the ends that are farthest apart, and can probably be integrated on PCBs of the devices that are farthest apart. The "backbone" with the termination on both ends should be much longer than the taps ("stubs") from the backbone to the devices. The physical wires, electrical specs (like differential signaling and voltage levels) are OSI layer 1.

CAN message collision avoidance is done in a CAN controller. This is available as a separate chip (with SPI interface), but it is also integrated as peripheral in the ESP32. At the start of each frame, every device wanting to send something starts sending their CAN ID (programmed into the device, must be unique). If a device has a lower ID, it gets priority by sending a dominant bit (logical 0, CAN_H and CAN_L are driven to different voltage levels) where other devices send a logical 1 (recessive bit, CAN_H and CAN_L are not driven making them return to equal voltage). If a device with a higher ID gets overruled this way, it will listen in this frame cycle and waits for the next frame to start before attempting to transmit its ID again. The frames also contain set amount of data and error checking bits.

There are frame types to request data (Remote frame), data containing (data frame), errror frame (when error is detected) and overload frame (indicating delay between data or remote frames is needed).

That is Link Layer (OSI layer 2).

OSI Layers 1 and 2 as implemented are standardized with ISO 11898-1.

ESP32 calls their implementation of this and maybe higher OSI layers TWAI: <https://docs.espressif.com/projects/esp-idf/en/v4.2.1/esp32/api-reference/peripherals/twai.html>

ESP32 CAN controller is not compatible with CAN FD (flexible data-rate), just classical CAN with 11-bit IDs (Standard Frame Format) and 29-bit IDs (Extended Frame Format).

The ESP32 TWAI controller depends on getting a receiving signal at the same time that it is sending something in order to work, because that is how it can determine if it is allowed to talk (CAN ID arbitration/priorities).

Higher OSI layers, like Network (OSI 3) and up are implemented in higher-layer protocols like CANopen. That implements flow control, multi-frame data segmentation, device addressing.

## hatplus-for-raspberrypi-5

[Schematic PDF](kicad/hatplus-for-raspberrypi-5/OUTPUTS/for-humans/hatplus-for-raspberrypi-5.pdf)

[ibom HTML](kicad/hatplus-for-raspberrypi-5/OUTPUTS/for-humans/ibom.html)

This board is effectively the mainboard for the mAIkroscope. It contains DC power input for the whole machine, switched power transmission to all motors, main coordinating microcontroller and interfacing with a Raspberry Pi.

The HAT is put on top of a Raspberry Pi 5 and can supply it with 5.1V 5A through the 40-pin header. The HAT will also fit on a NVIDIA Jetson development board, because its 40-pin header is designed to be compatible with Raspberry Pi's.

There are many comments for design choices, mechanisms, failsafes and links to external ressources in the [schematic PDF for our HAT](kicad/hatplus-for-raspberrypi-5/OUTPUTS/for-humans/hatplus-for-raspberrypi-5.pdf).

The microcontroller is a ESP32-WROOM-32E-N8 module with integrated PCB antenna, 8 MB flash. The used ESP32-D0WD-V3 chip in the module has 449 KB ROM, 520 KB SRAM and 16 KB SRAM in RTC core.

### Raspberry Pi HAT+ implementation (EEPROMS, HAT+ spec)

Our HAT is designed to comply with [Raspberry Pi HAT+ specifications](https://datasheets.raspberrypi.com/hat/hat-plus-specification.pdf).

However, it has the function of 2 types of HAT+s: Power supply and using the GPIO header for data exchange purposes.

The I2C addresses of EEPROMS on the HAT indicate the HAT+ class to the Raspberry Pi firmware. In multiple HAT+ stacked on one Raspberry Pi, there can be only one HAT of each class per spec and to avoid I2C address collisions.

The HAT has 2 EEPROM chips with functions and content:

| I2C Address | HAT+ class meaning            | EEPROM contents |
| ----------- | ----------------------------- | --------------- |
| 0x1010_000  | Standard (uses GPIO for data) | tbd             |
| 0x1010_000  | Power: MODE1 (can deliver 5A) | tbd             |

The content of the HAT can be custom content like serial numbers, manufacturer, or drivers/instructions for the Raspberry Pi OS on how to interface with the HAT. The format and mandatory fields are in the Raspberry Pi HAT+ spec document.

For our HAT, it would make sense to fill the EEPROMS for these functions:

- Ensure that the full power for USB devices is automatically activated (implementing a MODE1 HAT+).
- Add our company name, product name, board revision, unique serial number that we keep track of in the company
- Driver or interface/pin description to make the SPI CAN controller chip (MCP2515) available to python scripts via Linux.
- Descriptions of other GPIO pin functions, to be able to use them abstractly in future scripts: buspower_EN, ESP32 interface UART and flashing, etc
- Maybe things like hardware configuration options that should "just work", like what features and modules the mAIkroscope model has that it is built into, and factory calibration data for its modules

### Raspberry Pi pinout

For Raspberry Pi pin numbering and assignable or fixed functions, see [pinout.xyz](https://pinout.xyz).

In the table is the physical/board pin number, not GPIO number. The pin numbering on the header is odd-even.

| RPi | Function                                                           |
| --- | ------------------------------------------------------------------ |
| 3   | I2C-1_SDA connectable to ESP and XH_5V+I2C via solderjumper JP101  |
| 5   | I2C-1_SCL connectable to ESP and  XH_5V+I2C via solderjumper JP102 |
| 8   | UART_TX to ESP (parallel with USB-UART TX)                         |
| 10  | UART_RX from ESP (parallel with USB-UART RX)                       |
| 11  | ESP Auto-program circuit RTS                                       |
| 16  | buspower-off when HI                                               |
| 19  | CAN-Controller SPI PICO                                            |
| 21  | CAN-Controller SPI POCI                                            |
| 23  | CAN-Controller SPI SCK                                             |
| 24  | CAN-Controller SPI CS                                              |
| 26  | EEPROM I2C-0 SCL (HAT+ spec)                                       |
| 27  | EEPROM I2C-0 SDA (HAT+ spec)                                       |
| 32  | CAN-Controller Interrupt                                           |
| 36  | ESP Auto-program circuit DTR                                       |

### ESP32 pinout

Actual chosen model is ESP32-WROOM-32E-N8.

It is programmable via the USB-C port and CP2102 USB-Serial chip, or via Raspberry Pi UART (manual press of BOOT and RST necessary, or programming of the 2 Raspberry Pi GPIO to use the Auto-program circuit).

In the table are only GPIOs that are used and notable for the HAT. All GPIOs are also available at testpoints.

| GPIO | Function                                                     |
| ---- | ------------------------------------------------------------ |
| 4    | Buspower_off when HI                                         |
| 17   | CAN/TWAI Recieve                                             |
| 18   | CAN/TWAI Send                                                |
| 19   | Neopixel LED data                                            |
| 21   | I2C-1_SDA to XH_5V+I2C connector and solderjumpable to Raspi |
| 22   | I2C-1_SCL to XH_5V+I2C connector and solderjumpable to Raspi |
| 27   | Camera-IO-interface Cam In Line 0                            |
| 32   | Camera-IO-interface Cam Out Line 1                           |
| 33   | Camera-IO-interface Cam In/Out Line 2                        |

### Emergency STOP connector

There is a 3.5 mm TRS connector (stereo headphones) to connect an external box with a Emergency-STOP button and LEDs (optional). It is J501 and oriented out the back of the mAIkroscope.

A STOP button should be normally closed, and should open and lock when pressed. This button should be connected between Tip and Ring of the TRS connector. This button is required for Buspower (5V or 12V out of the respective XH jacks) to turn on.

LEDs can be placed in or on the external box so it is easily visible in dark conditions. The LEDs have a budget of 3.3V and 20 mA, and resistors should be included in the box. If more amperage is pulled, the HAT may recognize it as STOP button press. Connect LEDs with High side at Tip and Low side at Sleeve of TRS connector. LEDs will always be lit regardless of STOP button state.

### HAT: Terminating CANBUS or activating CAN activity indicator LED

Close JP jumpers by making a solder bridge between the 2 pads. To open a NO (normally open) solderjumper again, wipe, wick or suck away the solder bridge. To open a NC (normally closed) solderjumper, cut the trace between the pads with a knife very carefully and not cutting too deep. Design flaw: Cutting too deep exposes the copper of the inner layers and may cut or short traces on the inner layers. The cut should be planned in the PCB editor, and the trench should be cleaned up and filled with solder mask after cutting. In future, use 0-Ohm resistors for NC.

| Operation    | Effect                                                                                          |
| ------------ | ----------------------------------------------------------------------------------------------- |
| Close JP1001 | Terminates CANBUS on the board by connecting CAN_H and CAN_L through 120 Ohm resistor           |
| Close JP1002 | Red LED D1001 lights when CAN bus is in dominant state (logical 0, lines at different voltages) |

### Disabling communication or power-switching functions

This is only relevant for troubleshooting and may defeat safety functions.

| Operation   | Effect                                                                                                                 |
| ----------- | ---------------------------------------------------------------------------------------------------------------------- |
| Close JP201 | ESP and Raspberry Pi can no longer turn off buspower via GPIO pin                                                      |
| Close JP601 | Override all buspower-off sources including Emergency-STOP button. Button SW601 can still momentary turn-off buspower. |
| Open JP901  | Disconnect Raspberry pin from RTS line of CP2102 and Auto-program circuit                                              |
| Open JP902  | Disconnect Raspberry pin from DTR line of CP2102 and Auto-program circuit                                              |

## stepper-backpack

[Schematic PDF](kicad/stepper-backpack/OUTPUTS/for-humans/stepper-backpack.pdf)

[ibom HTML](kicad/stepper-backpack/OUTPUTS/for-humans/ibom.html)

stepper-backpack is a PCB to fasten to the back of a NEMA 11 stepper motor. It enables the motor-PCB-assembly to be controlled via CAN with high-level commands and implements absolute feedback.

- Glue a circular magnet to the end of the stepper motor's axle
- Mount the PCB to the back of the motor using 3 pcs of M2.5 screws with cylindrical standoffs between board and motor. The standoffs should be about 2.5mm long. The PCB should fit completely behind the motor.
- Connect the motor's electrical connections (coils) to the PCB via screw terminal blocks. A and B labels correspond to the 2 coils in the motor.
- Connect it to a 12V supply and CAN via JST XH 4-pin connector
- The PCB controls the motor with a TMC2209 stepper motor driver
- A magnetometer on the PCB measures axle position and supply feedback for accurate positioning
- A XIAO ESP32S3 plugged in to the PCB can accept high-level commands (go to a position) and handle autonomous homing and stepping control (low level control of the stepper motor driver)
- The high-level interface can supply information about motor load, command success/status, fail state, etc.
- Endstop can be connected to a XIAO pin, 3.3V and GND with JST ZH 3-pin connector.

### Pinout

The different XIAO models connect to different ESP GPIOs, and strapping pins, pins with glitches or pins with default pullups/pulldowns may be different between ESP models in the XIAO format.

| XIAO pin | Function                     |
| -------- | ---------------------------- |
| D0       | Endstop                      |
| D1       | CAN Receive / SCL on old bus |
| D2       | CAN Send / SDA on old bus    |
| D3       | Motor driver DIAG output     |
| D4       | I2C SDA to encoder           |
| D5       | I2C SCL to encoder           |
| D6       | UART send to motor driver    |
| D7       | UART recv from motor driver  |
| D8       | Motor direction              |
| D9       | Motor step                   |
| D10      | Motor driver enable          |

### Current sensing and current setting

Rsense (or R_SENSE) is __0.2 Ohm__. This is the value of the sense resistance connected to BRA and BRB of the TMC2209.

The current limit can be set by setting the __Vsense__ value in the TMC, which is the sensitivity of the current measurement. Setting this, with the 0.2 Ohms of actual resistance on stepper-backpacker, yields:

- Vsense=0 (low sensitivity curr sense setting): 1.4A peak, 1A RMS
- Vsense=1: 0.8A peak, 0.55A RMS

### Converting Rev. C from 12V+CAN to 5V+I2C

Make sure there are pullups (4.7k) to 3.3V somewhere on both I2C lines.

Use the ibom.html to find the correct solderjumpers on the board.

Close JP jumpers by making a solder bridge between the 2 pads. Open R 0-resistors by unsoldering them or snapping them with pliers.

| Operation   | Effect                                                                   |
| ----------- | ------------------------------------------------------------------------ |
| Close JP102 | CANBUS_P connects directly to XIAO GPIO (as I2C-1_SDA)                   |
| Close JP103 | CANBUS_N connects directly to XIAO GPIO (as I2C1_SCL)                    |
| Close JP501 | Connects CAN transceiver Rs to 3.3V to STBY transmitter driver           |
| Open R502   | Disconnect still-active CAN receiver oupoutput from XIAO pin D1          |
| Open R501   | Disconnects CAN transceiver VCC power input from 3.3V                    |
| Close JP101 | Connects 12V and 5V power nets (Warning: Do not connect 12V when closed) |

### Terminating CANBUS or activating CAN activity indicator LED

| Operation   | Effect                                                                                         |
| ----------- | ---------------------------------------------------------------------------------------------- |
| Close JP502 | Terminates CANBUS on the board by connecting CAN_H and CAN_L through 120 Ohm resistor          |
| Close JP503 | Red LED D501 lights when CAN bus is in dominant state (logical 0, lines at different voltages) |

## Laser-interface

This board can control a laser or LEDs and has 4 channels. It connects to the XH_12V+CAN backbone, has a XIAO to accept CAN commands and generate PWM signals, and has connectors for interlock sources. The interface to the laser is 4x PWM signal between 0V and 3.3V (LO should mean off), and 12V power.

### XIAO pinout

I is intended as input to the XIAO. O is intended as output.

| XIAO pin | XIAO ESP32S3 pin | Board Function                                                                  |
| -------- | ---------------- | ------------------------------------------------------------------------------- |
| D0       | GPIO_01          | I: LO when interlock tripped (enable pullup), O: pull LO to light keyswitch-LED |
| D1       | GPIO_02          | O: signal_1                                                                     |
| D2       | GPIO_03          | O: signal_2                                                                     |
| D3       | GPIO_04          | O: CAN-SEND                                                                     |
| D4       | GPIO_05          | O: signal_3                                                                     |
| D5       | GPIO_06          | O: signal_4                                                                     |
| D6       | U0TXD/GPIO_43    | Unused, available on J1101                                                      |
| D7       | U0RXD/GPIO_44    | Unused, available on J1101                                                      |
| D8       | GPIO_07          | Unused, available on J1101                                                      |
| D9       | GPIO_08          | I: LO when interlock has power (keyswitch in ON position)                       |
| D10      | GPIO_09          | I: CAN-RECV                                                                     |

### Keyswitch specifications and connections

J102 is a 3-pin screw terminal to connect a key-switch and a red LED.

The key-switch should be a single-pole single-throw key-operated switch where the key can only be removed in OFF position. It switches less than 1 mA at 3.3V. In the ON position, the switch should connect pin 2 and 3 of J102.

The LED indicates when the interlock has triggered and the user needs to reset the interlock by turning off and on the keyswitch. It has 200 Ohms in series at 3.3V, so a red LED will be driven with around 7 mA. An ESP GPIO can light this LED at half current. The red LED on the board close to the output terminal has the same states as the external LED. An LED should directly be connected to J102 with Anode (+) on pin 2, and Cathode (-) on pin 1.

### Interlock

The interlocks ensure that a signal can only pass from the ESP to the laser if:

- The keyswitch is in the ON position
- 12V power is stable (aka Emergency-stop not pushed)
- A magnet switch is closed indicating that something like a laser-safety hood is covering the device
- An endstop or optical endstop is pressed indicating that the modules are fully inserted, the hood is closed, etc.

#### Interlock behavior and status inticators

The interlock has to be powered on by turning the keyswitch ON. It will then watch all the interlock sources, and trigger if one of the sources has an unsafe state.

If the interlock has been triggered, it will stop transmitting any signal to the laser, and the red LED by the keyswitch and by the output terminals will be lit. The interlock will stay triggered until it is reset by turning the keyswitch OFF and ON again.

If the interlock is active and not triggered, signals from the ESP (signal_1-4) will be transmitted to the output terminal block. Probably only binary signals like PWM will work. If the interlock is transmitting, the green LED by the output terminals will be lit, but the red LED next to it will not be lit.

#### Interlock sources

__Keyswitch (J102)__: The keyswitch switches power to the latch circuit of the signals interlock. If this is ON, the green LED close to the output terminals will be lit.

__12V-OK (internal)__: The 12V input has to stay above 11.3V. If power falls below that, the 12V power to the laser will be turned off, and the interlock for the signals will be triggered. This enables early detection when the Emergency Stop has been pressed and the power is interrupted. When the 12V to the laser is ON, the green LED below the XIAO will be lit.

__Endstop (J103)__: The 3-pin screw terminal J103 provides GND, signal, and 3.3V. The signal has to be HI for normal operation, like when the modules are fully inserted or when the safety hood is closed. If the signal pin is LO or floating, it will trigger the interlock. Because there is constant 3.3V and GND available, optical endstops can be used.

__Magnet Switch (J104)__: On the 2-pin screw terminal J104, a simple magnet switch (reed switch) or other simple switch can be connected. The switch should close in the presence of a magnet, and be open otherwise. For normal operation, a magnet can be fixed to the safety hood, and the switch in the base where the magnet will be close if the hood is closed (safe). Other switches can also be used. When the contacts are closed (shorted), it is safe, and when the switch is opened, the interlock triggers.

#### Interlock overrides

Parts of the interlock can be deactivated so that no condition at this interlock source will trigger the interlock. This way, the laser-interface can be configured to the types of safety devices available, when it is integrated into a microscope.

To override parts of the interlock, turn on one or multiple switches inside the dipswitch __SW701__ to the side labeled ON. This will close the switch and assume SAFE regardless of the actual state of the interlock source. No state on the respective interlock source will trigger the interlock.

The individual switches of the dipswitch are numbered. All interlock sources are active if all switches are OFF (set to the side opposite of the side labeled ON).

| SW701 switch number | effect when ON                                                                                                      |
| ------------------- | ------------------------------------------------------------------------------------------------------------------- |
| 1                   | Magnet switch J104 overridden                                                                                       |
| 2                   | 12V-OK interlock triggering overridden and 12V output to laser always ON                                            |
| 3                   | Hood Endstop switch J103 overridden                                                                                 |
| 4                   | Overrides whole interlock including keyswitch. Signals will always be passed, but 12V-OK still switches laser power |
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

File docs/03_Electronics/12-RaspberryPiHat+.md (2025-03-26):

# HAT+

This is a HAT for the Raspberry Pi 5 that adapts the Raspberry pi to an esp32 that in turn talks to auxilary components like motors and illumination modules via CAN Bus and I2C (optionally).

## Pinout

This is the hat's pinout on:
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

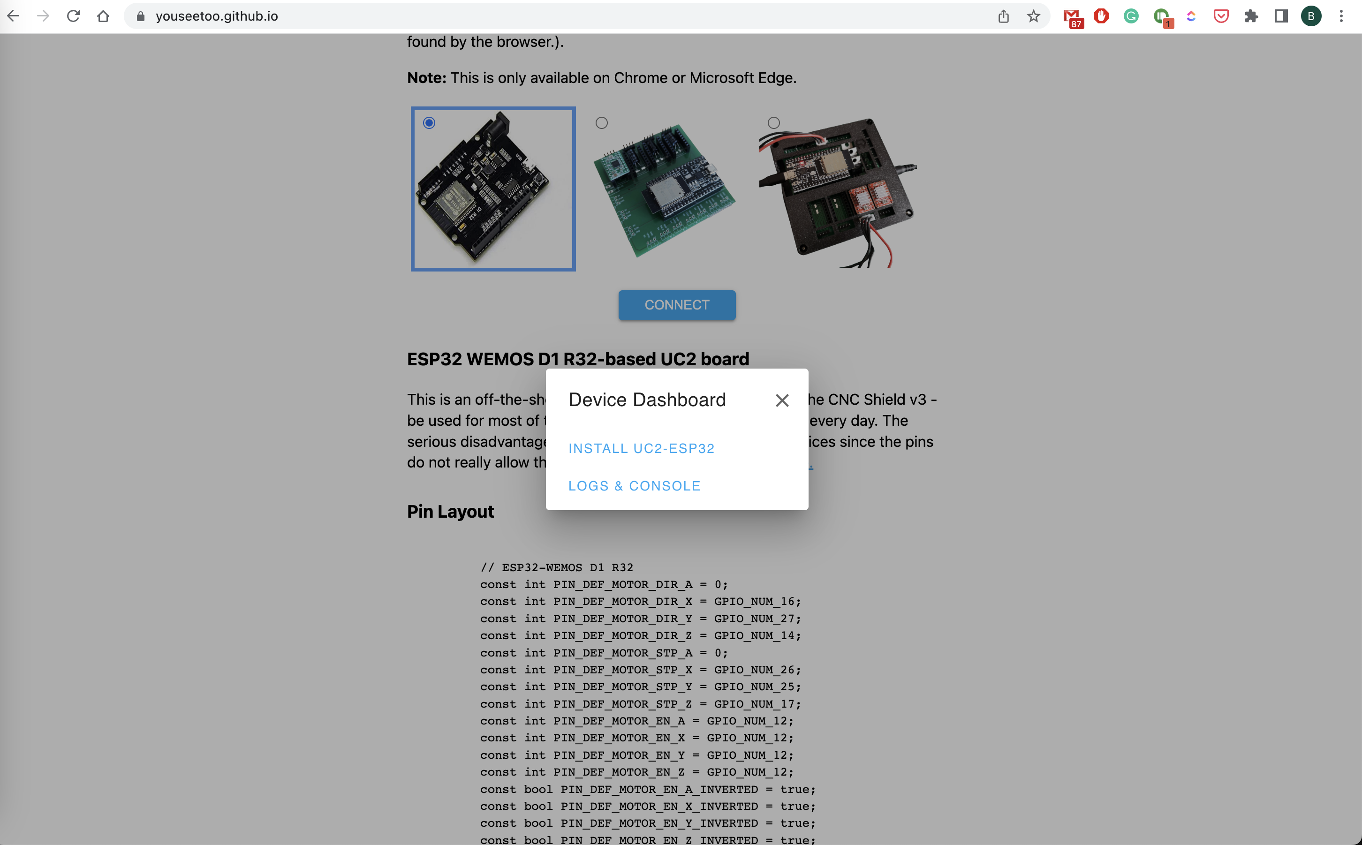
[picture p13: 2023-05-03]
docs/03_Electronics/IMAGES/flashingtool_8.png

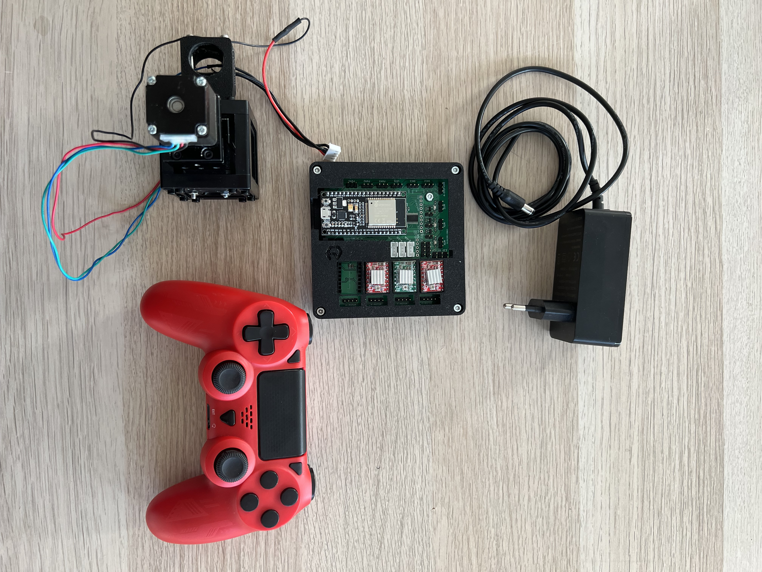
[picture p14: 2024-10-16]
docs/01_Toolboxes/02_DiscoveryElectronics/IMAGES/EXP_1_Serial/Photo_Control_Stage.jpg

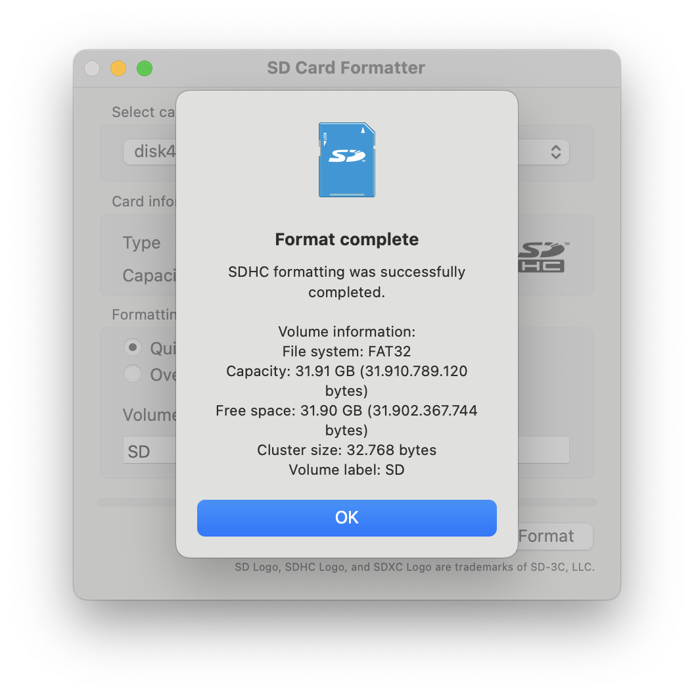
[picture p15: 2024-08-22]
docs/01_Toolboxes/02_DiscoveryElectronics/IMAGES/OpenUC2xSeeed/SDCard_2.png

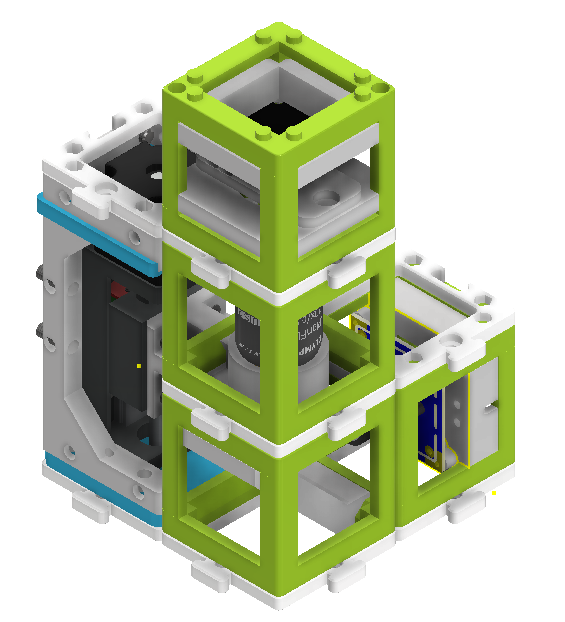
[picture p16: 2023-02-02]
docs/01_Toolboxes/02_DiscoveryElectronics/IMAGES/Incubatormicroscpoe2.png

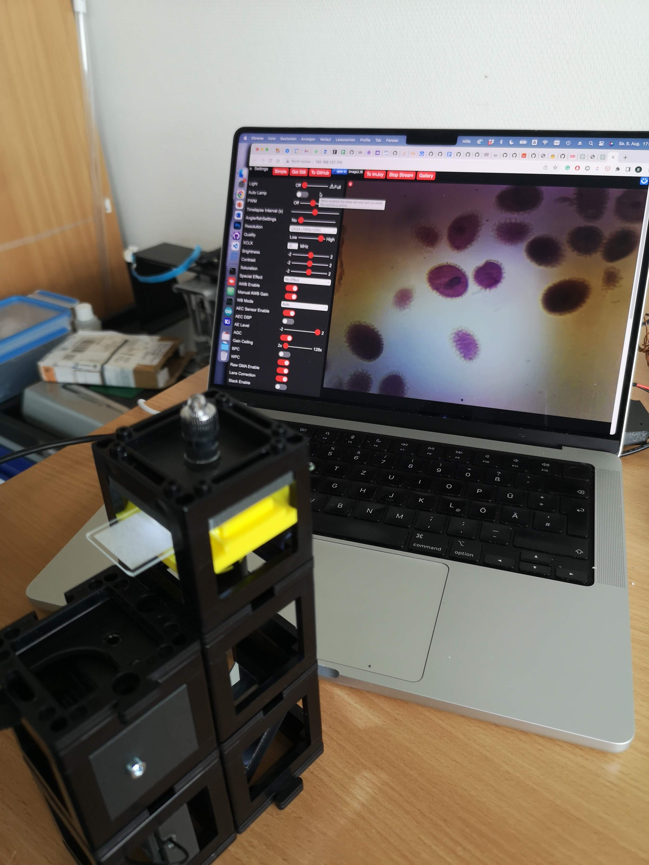
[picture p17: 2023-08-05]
docs/01_Toolboxes/02_DiscoveryElectronics/IMAGES/seeed/Seeedmicroscope_40.jpg

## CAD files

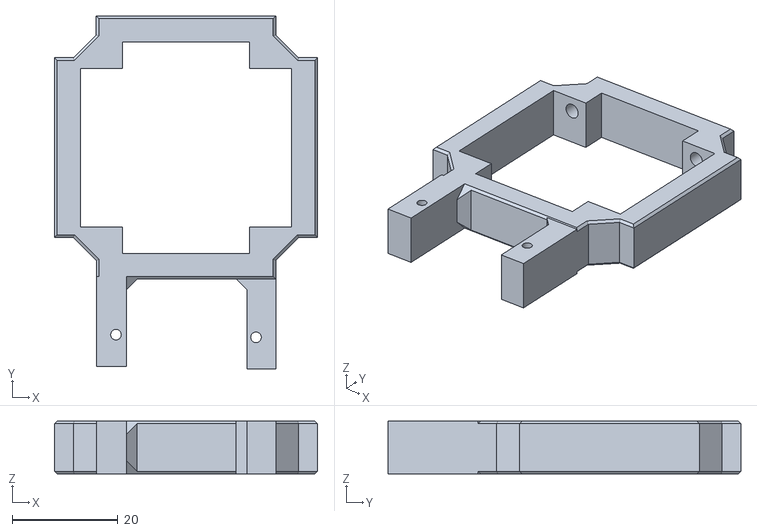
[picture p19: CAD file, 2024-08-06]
docs/01_Toolboxes/02_DiscoveryElectronics/IMAGES/OpenUC2xSeeed/Assembly_Cube_Linear_Sampleslide_Servo_20_Cube_Insert_linearslide_servodriven_v2_6.stl
49.8 x 66.8 x 10.00

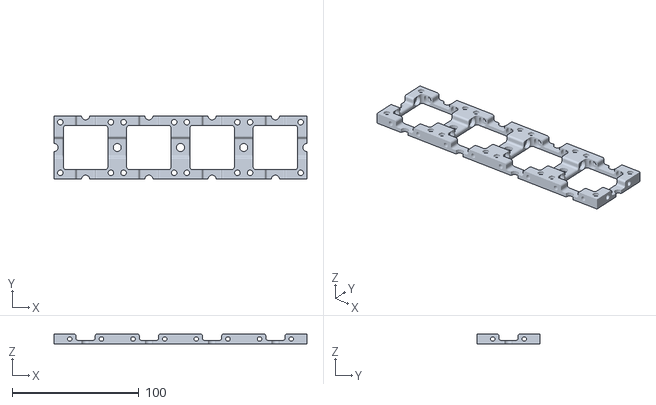
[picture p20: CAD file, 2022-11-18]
static/DISCOVERY_BASE/BUILDME/05_Assembly_base_4x1.stl
200.0 x 50.0 x 8.00

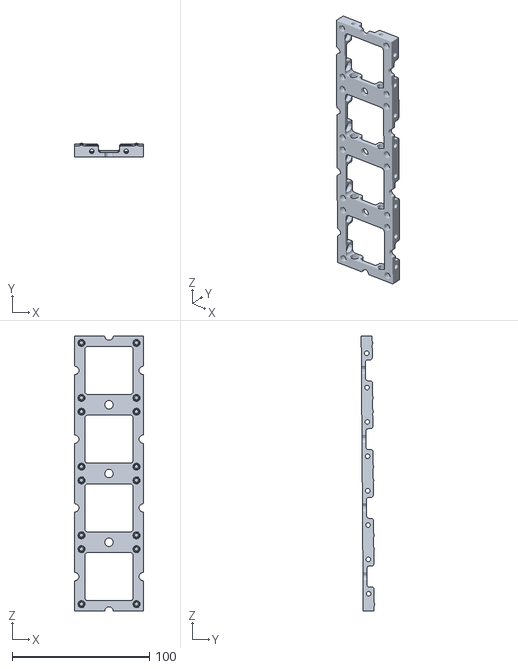
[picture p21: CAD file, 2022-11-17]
static/POLARISATION/ACTIVE/Assembly_Cube_Baseplate_4x1_v2.stl
50.0 x 9.94 x 200.1

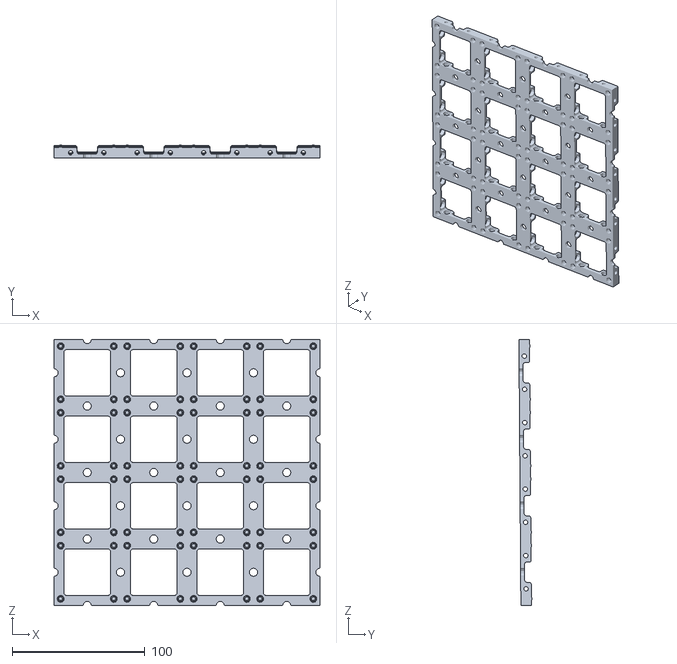
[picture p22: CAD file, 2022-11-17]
static/POLARISATION/NEWTON/Assembly_Cube_Baseplate_4x4_v2.stl
200.0 x 9.94 x 200.1

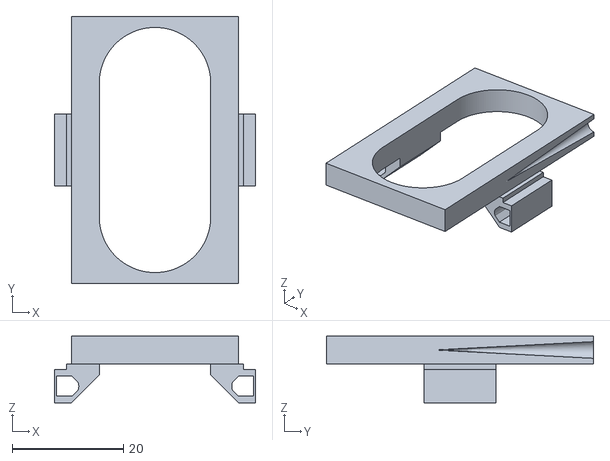
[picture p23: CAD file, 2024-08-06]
docs/01_Toolboxes/02_DiscoveryElectronics/IMAGES/OpenUC2xSeeed/Assembly_Cube_Linear_Sampleslide_Servo_20_Cube_Insert_linearslide_servodriven_slide_v2_8.stl
36.1 x 48.0 x 12.0

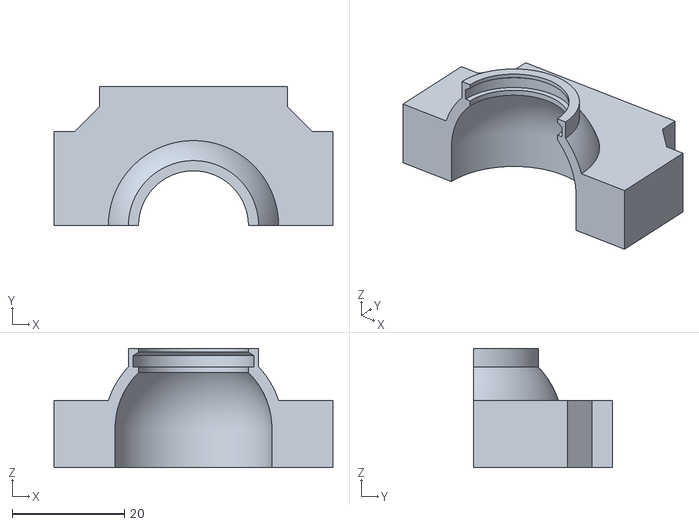
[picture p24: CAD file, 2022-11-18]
static/DISCOVERY_BASE/BUILDME/33_Assembly_Cube_Eyeball_v2_20_Cube_Insert_Eye_Lens_2.stl
49.8 x 24.9 x 21.3

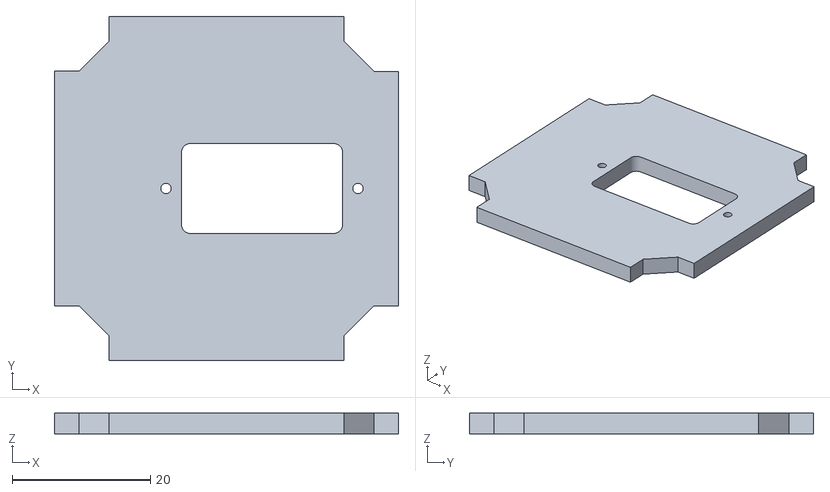
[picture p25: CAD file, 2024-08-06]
docs/01_Toolboxes/02_DiscoveryElectronics/IMAGES/OpenUC2xSeeed/Assembly_Cube_MiniServoCenteredFocus_v3_20_Cube_Insert_MiniServoFocus_5.stl
49.8 x 49.8 x 3.00

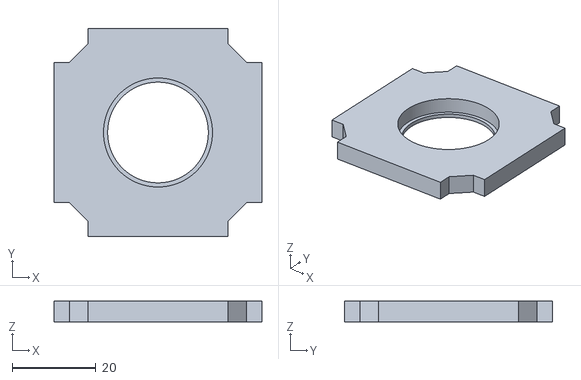
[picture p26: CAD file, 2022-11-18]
static/DISCOVERY_BASE/BUILDME/13_1inch_Assembly_Insert_Lens_mount_fixed_20_Lens_holder.stl
49.8 x 49.8 x 5.00

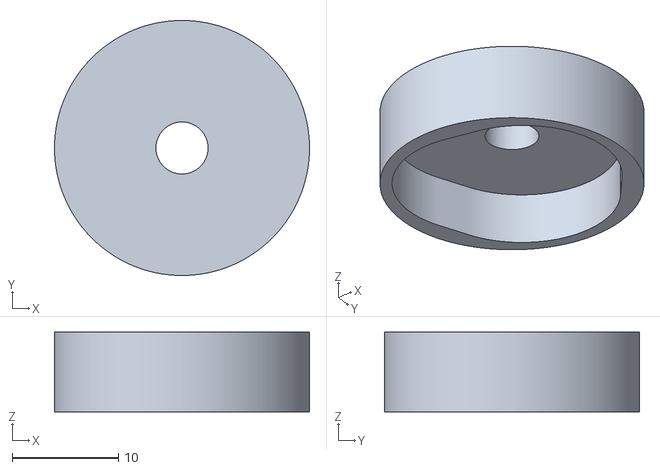
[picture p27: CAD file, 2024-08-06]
docs/01_Toolboxes/02_DiscoveryElectronics/IMAGES/OpenUC2xSeeed/Assembly_Cube_MiniServoCenteredFocus_v3_20_Cube_Insert_MiniServoFocus_Knobadapter_20mm_6.stl
24.0 x 24.0 x 7.50

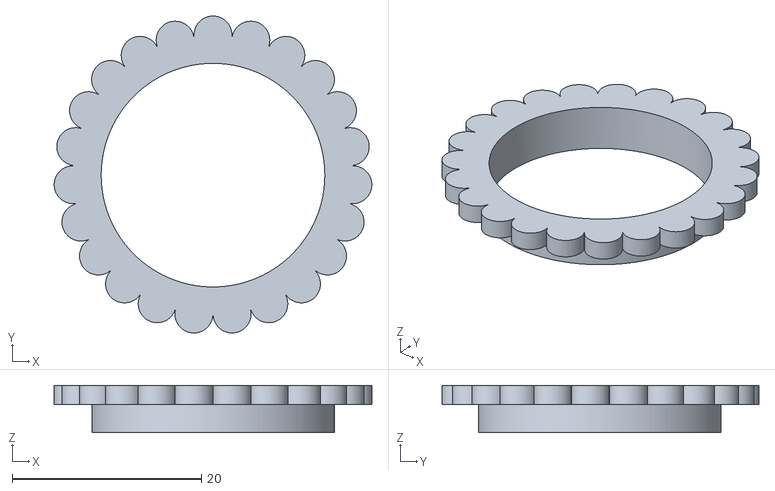
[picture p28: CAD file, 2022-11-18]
static/DISCOVERY_BASE/BUILDME/14_1inch_Assembly_Insert_Lens_mount_fixed_20_Lens_holder_clamp.stl
33.5 x 33.5 x 5.00

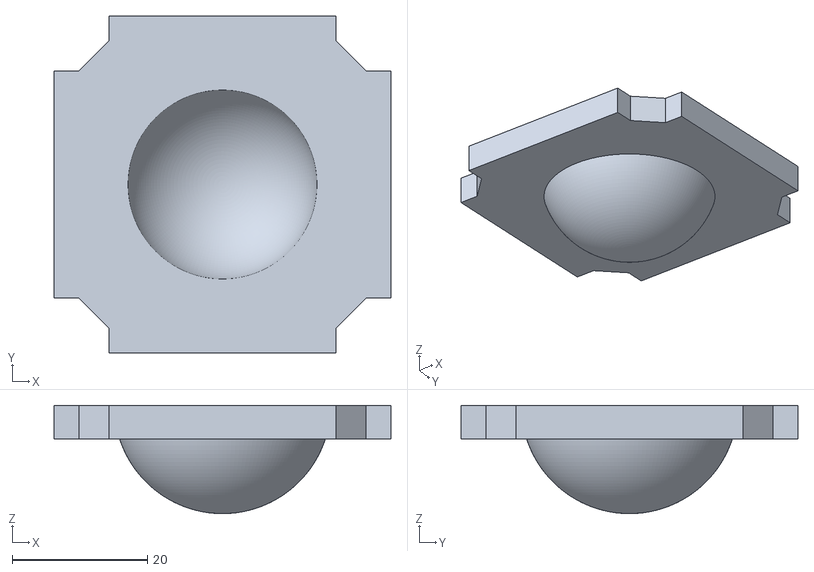
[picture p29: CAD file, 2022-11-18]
static/DISCOVERY_BASE/BUILDME/32_Assembly_Cube_Eyeball_v2_20_Cube_Insert_Eye_1.stl
49.8 x 49.8 x 16.0

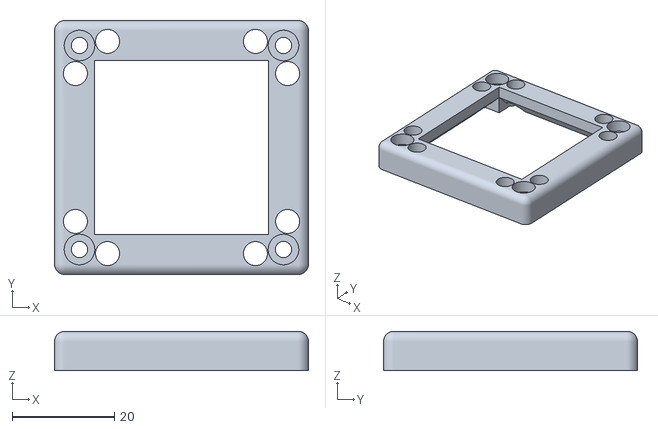
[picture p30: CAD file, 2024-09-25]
docs/00_General/01_ModuleDeveloperKit/STL/UC2_v3_10_Lid_1x1_v3.stl
49.8 x 49.8 x 7.70

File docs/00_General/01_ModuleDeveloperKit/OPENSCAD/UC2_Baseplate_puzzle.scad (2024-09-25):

//Cube insert: Baseplate puzzle piece 

/* [User Parameters] */
//screw offset
scr_offset = 0; //[-0.1:0.1:0.3]
//magnet offset
mag_offset = 0; //[-0.1:0.1:0.3]
//male puzzle offset
puzzle_m_offset = 0; //[0:0.1:0.4]
//female puzzle offset
puzzle_f_offset = 0; //[0:0.1:0.4]


/* [Hiden] */
$fn = 80;
eps = .002;
a = 50; //UC2 unit size
h = 5; //height of the baseplate
b = 34; //size of the inner empty space
mag = 4.85; //magnet hole diameter default
scr = 5.3; //screw hole diameter default
s1 = 10.5; //screw hole to side distance 1 (x,y)
s2 = 4.2; //screw hole to side distance 2 (x,y)
r1 = 2; //radius of fillets
m6_1 = 5; //hole for M6 screw diameter
m6_2 = 8; //hole for M6 screw head diameter
m6_3 = 3; //hole for M6 screw head depth
m6_4 = 4; //hole for M6 screw to side distance
puzz1 = 10; //puzzle protrusion neck thickness
puzz2 = 1.5; //puzzle protrusion neck length
puzz3 = 0.5; //puzzle protrusion distance 3
puzz4 = 0.075; //male to female puzzle protrusion offset 
puzz5 = 0.41; //puzzle protrusion radius of fillets

baseplate_puzzle ();

module baseplate_puzzle () {
    difference () {
    union () { //four corners together
        corner();
        translate([a,0,0]){rotate([0,0,90]){corner();}}
        translate([0,a,0]){rotate([0,0,270]){corner();}}
        translate([a,a,0]){rotate([0,0,180]){corner();}}
        translate([a/2-puzz1/2,-(r1+puzz2),0]){puzzle_m();} //male puzzle
        translate([-(r1+puzz2),a/2+puzz1/2,0]){rotate([0,0,270]){puzzle_m();}} //male puzzle
    }
    translate([a/2,m6_4,-eps/2]){m6_hole();} //M6 screw hole
    translate([m6_4,a/2,-eps/2]){m6_hole();} //M6 screw hole
    translate([a/2-puzz1/2,a-r1-puzz2,0]){puzzle_f();} //female puzzle
    translate([a-r1-puzz2,a/2+puzz1/2,0]){rotate([0,0,270]){puzzle_f();}} //female puzzle
    }
}
module corner () {
    union () {
        difference () {
            cube([a/2,a/2,h]);
            difference () { //outer corner fillet
                translate([-eps,-eps,-eps/2]){cube([r1,r1,h+eps]);}
                translate([r1,r1,-eps/2]){cylinder(h+2*eps,r=r1);}
            }
            translate([(a-b)/2,(a-b)/2,-eps/2]){cube([b/2+eps,b/2+eps,h+eps]);}
            translate([h,h,-eps/2]){cylinder(h+eps,d=mag+mag_offset);} //hole for magnet
            translate([s1,s2,-eps/2]){cylinder(h+eps,d=scr+scr_offset);} //hole for snap fit
            translate([s2,s1,-eps/2]){cylinder(h+eps,d=scr+scr_offset);} //hole for snap fit
        }
        translate([(a-b)/2,(a-b)/2,0]){ //inner corner fillet
            difference () {
                translate([-eps,-eps,]){cube([r1,r1,h+eps]);}
                translate([r1,r1,-eps/2]){cylinder(h+2*eps,r=r1);}
            }
        }
    }
}
module m6_hole () {
    union () {
        cylinder(h+eps,d=m6_1);
        translate([0,0,h-m6_3]){cylinder(m6_3+eps,d=m6_2);}
    }
}
module puzzle_m () {
    union () {
        cylinder(h+eps,r=r1-puzzle_m_offset);
        translate([puzz1,0,0,]){cylinder(h,r=r1-puzzle_m_offset);}
        translate([0,-r1+puzzle_m_offset,0]){cube([puzz1,2*(r1-puzzle_m_offset),h]);}
        translate([puzzle_m_offset,r1-puzzle_m_offset,0]){cube([puzz1-2*puzzle_m_offset,puzz2+puzzle_m_offset,h]);}
        translate([puzz1-puzzle_m_offset,r1-puzzle_m_offset,0]){difference () {
                translate([-eps,-eps,0]){cube([puzz3,puzz3,h]);}
                translate([puzz3,puzz3,-eps/2]){cylinder(h+eps,r=puzz3);}
            }}
        translate([puzzle_m_offset,r1-puzzle_m_offset,0]){rotate([0,0,90]){difference () {
                translate([-eps,-eps,0]){cube([puzz3,puzz3,h]);}
                translate([puzz3,puzz3,-eps/2]){cylinder(h+eps,r=puzz3);}
            }}}
    }
}
module puzzle_f () {
    union () {
        cylinder(h+eps,r=r1+puzz4+puzzle_f_offset);
        translate([puzz1,0,-eps/2]){cylinder(h+eps,r=r1+puzz4+puzzle_f_offset);}
        translate([0,-r1-puzz4-puzzle_f_offset,-eps/2]){cube([puzz1,2*(r1+puzz4+puzzle_f_offset),h+eps]);}
        translate([-1.25*puzzle_f_offset,r1+puzz4+puzzle_f_offset,-eps/2]){cube([puzz1+2*puzz4+2*puzzle_f_offset,puzz2,h+eps]);}
        translate([puzz1+2*puzz4+0.75*puzzle_f_offset,r1+0.5*puzz4+0.75*puzzle_f_offset,0]){difference () {
                translate([-eps,-eps,-eps/2]){cube([puzz5,puzz5,h+eps]);}
                translate([puzz5,puzz5,-eps/2]){cylinder(h+2*eps,r=puzz5);}
            }}
        translate([puzz4-1.5*puzzle_f_offset,r1-puzz4+1.25*puzzle_f_offset,0]){rotate([0,0,90]){difference () {
                translate([-eps,-eps,-eps/2]){cube([puzz5,puzz5,h+eps]);}
                translate([puzz5,puzz5,-eps/2]){cylinder(h+2*eps,r=puzz5);}
            }}}
    }
}

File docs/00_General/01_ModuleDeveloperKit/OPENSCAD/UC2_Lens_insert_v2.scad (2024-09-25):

//Cube insert: Lens holder with clamp 

/* [User Parameters] */
//Lens diameter - measure the diameter of your lens carefully and insert the value in millimetres. The holder can be used for lenses with a diameter from 9 mm to 42 mm.
lens_diameter = 25.4; //[9:0.01:42]
//Edge thickness - measure the thickness of your lens as close to the outer edge as possible.
lens_edge_thickness = 1.5; //[0.5:0.01:9]
// Which part would you like to print?
part = "first"; // [first:Both - Holder AND Clamp,second:Holder ONLY,third:Clamp ONLY]
// Is this insert for a 3D printed cube or for a cube produced by injection molding?
3D_printed_cube = "3Dprint"; // [3Dprint,IM]
// Write the focal length of the lens that you will put in this holder. Input: number in millimetres, no units, add '-' for a negative lens. 
focal_length = "f"; 

/* [Hiden] */
$fn = 80;
eps = .002;
a = 49.8;
b = 33.6;
c = 6.28;
d = 53.8;
h = lens_edge_thickness < 4.1 ? 5 : 5+(lens_edge_thickness-3); //holder height
h1 = 3; //clamp rims height
t = 1.5; //clamp ring thickness
IM_offset = 3D_printed_cube == "3Dprint" ? 0 : 0.2;

print_part();

module print_part() {   //choose part to print holder/clamp/both
	if (part == "first") {
		lens_holder();
        lens_clamp();
	} else if (part == "second") {
		lens_holder();
	} else if (part == "third") {
		lens_clamp();
	} 
}

module lens_holder () {
    difference(){
        union() {   //basic insert design
            cube([a,b+2*IM_offset,h], center=true);
            cube([b+2*IM_offset,a,h], center=true);
            rotate(a=[0,0,45]){
                cube([c,d+2*IM_offset,h], center=true);
            }
            rotate(a=[0,0,-45]){
                cube([c,d+2*IM_offset,h], center=true);
            }
        }
        union() {
            cylinder(h+eps,d=lens_diameter-2, center = true); //hole
            translate([0,0,(h-lens_edge_thickness)/2]){
                cylinder(lens_edge_thickness+eps,d=lens_diameter+0.7, center = true); //rim to hold the lens
            }
        }
            translate([0,-24,((h+h1-0.1)/2-2.45)]){
                linear_extrude(height = 2) text(focal_length, size=5, font="Arial black:style=Regular",halign = "center", spacing=1);
            }
    }
    translate([0,0,(h+h1-0.1)/2]){  //rim for the clamp
        difference(){
                cylinder(h1+0.1,d1=lens_diameter+2.9, d2=lens_diameter+1.9, center = true);
                cylinder(h1+0.1+eps,d=lens_diameter+0.7, center = true);
        }
    }
}

module lens_clamp() {
    translate([a/2+lens_diameter/2+7,0,-(h-t)/2]){
        difference(){   //bottom ring
            cylinder(t, d=lens_diameter+4.9, center = true);
            cylinder(t+eps, d=lens_diameter-1, center = true);
        }
        translate([0,0,+(h1+t)/2]){
            difference(){   //outer rim
                cylinder(h1,d=lens_diameter+4.9, center = true);
                cylinder(h1+eps,d=lens_diameter+2.9, center = true);
            }
            difference(){   //inner rim
                cylinder(h1,d=lens_diameter+0.5, center = true);
                cylinder(h1+eps,d=lens_diameter-1, center = true);
                }
            }
        }
    }

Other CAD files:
docs/00_General/01_ModuleDeveloperKit/CAD/10_Cube_1x1_IM.dwg
docs/00_General/01_ModuleDeveloperKit/INVENTOR/00_BallMagnets_5mm.ipt
docs/00_General/01_ModuleDeveloperKit/INVENTOR/10_Base_puzzle_v3.ipt
docs/00_General/01_ModuleDeveloperKit/INVENTOR/10_Cube_1x1_IM.ipt
docs/00_General/01_ModuleDeveloperKit/INVENTOR/10_Cube_1x1_v3.ipt
docs/00_General/01_ModuleDeveloperKit/INVENTOR/10_Lid_1x1_v3.ipt
docs/00_General/01_ModuleDeveloperKit/INVENTOR/20_Cube_Insert_Template_fullcube_v3.ipt
docs/00_General/01_ModuleDeveloperKit/INVENTOR/20_Cube_Insert_Template_v3.ipt
docs/00_General/01_ModuleDeveloperKit/INVENTOR/Assembly_Cube_Template_v3.iam
docs/00_General/01_ModuleDeveloperKit/INVENTOR/Assembly_Cube_empty_1x1_withBase_v3.iam
docs/00_General/01_ModuleDeveloperKit/INVENTOR/DIN 912 - M3 x 0.5 x 12 x 10.75.ipt
docs/00_General/01_ModuleDeveloperKit/INVENTOR/ISO 4026 - M5 x 8 - ISO.ipt
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

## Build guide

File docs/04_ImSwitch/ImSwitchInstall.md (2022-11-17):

---
id: ImSwitchInstall
title: Install ImSwitch
---

### What will you learn?
- How to install the main GUI software to control the Optics components
- How to intsall the drivers

## Download the software
Duration: 1

Please go to our ImSwitch Repository and download the latest Build-artefact:

[GitHub Actions -> "bundle"](https://github.com/openUC2/ImSwitch/actions/runs/3093615193)

<p align="center">

</p>

## Extract the ZIP folder
Duration: 2

Right click on the downloaded ZIP folder and select "extract all". This may take a while.

<p align="center">

</p>

## Download and Install the drivers for the Camera/UC2 Electronics board

**Electronics Board (CH340)**

For the CH340 driver, please follow [these instructions](https://sparks.gogo.co.nz/ch340.html)

The driver is available [here](https://sparks.gogo.co.nz/assets/IMSWITCH/_site_/downloads/CH34x_Install_Windows_v3_4.zip)

```
Download the Windows CH340 Driver
Unzip the file
Run the installer which you unzipped
In the Device Manager when the CH340 is connected you will see a COM Port in the Tools > Serial Port menu, the COM number for your device may vary depending on your system.
```

**Electronics Board (CP210x)**

The driver for the CP210x is available [here](https://www.silabs.com/developers/usb-to-uart-bridge-vcp-drivers)

```
Download the Windows CP210x Driver
Unzip the file
Run the installer which you unzipped
In the Device Manager when the CP210x is connected you will see a COM Port in the Tools > Serial Port menu, the COM number for your device may vary depending on your system.
```

**Daheng Imaging Cameras**

Download the *Windows SDK USB2+USB3+GigE (including Directshow + Python) Galaxy V1.18.2208.9301* for the Daheng USB3 Cameras from the [Get-Cameras Website](https://www.get-cameras.com/requestdownload)

<p align="center">

</p>

Install the packages on your computer.

Duration: 2

## Prepare ImSwitch

1. Connect the Camera with your computer (optionally test its proper functioning using Daheng Galaxy Viewer(x64)) using the USB3 cable
2. Connect the UC2 electronics with the computer (USB micro) and hook up the 12V power supply with the power connection
3. Check if you can see the USB COM Port in your device manager:

<p align="center">

</p>

Duration: 2
## Install the UC2 ImSwitch Configurations

In order to use the UC2 Hardware and the Daheng USB Camera, you need the UC2 config files. Please go to https://github.com/openUC2/ImSwitchConfig/tree/stable and download the Repository as a zip file following this [link](https://github.com/openUC2/ImSwitchConfig/archive/refs/heads/stable.zip).

Once it has been downloaded, unzip it to `C:\Users\YOURUSERNAME\Documents\ImSwitchConfig`

It should look like this:

<p align="center">

</p>

Duration: 2
## Start ImSwitch

1. Open a Windows Terminal by typing `WIN+R`, then type `CMD` and hit enter.

<p align="center">

</p>

2. in the Windows Terminal navigate to the folder where you downloaded the softare - e.g. `cd C:\Users\UC2\Downloads\imswitch-windows-latest\ImSwitch` and hit enter
3. start the executable **BUT** we need to add one comment in advance:`set SETUPTOOLS_USE_DISTUTILS=stdlib`
3. Type `ImSwitch.exe` and hit enter, the executable will open the ImSwitch GUI

<p align="center">

</p>

If everything has been configured correctly, the GUI should open and look like this. Additional information on its functionality can be found in the Read-The-Docs:  https://imswitch.readthedocs.io/en/stable/
<p align="center">

</p>

If you have any additional questions or issues, please post them in the [ISSUE section here](https://github.com/openUC2/ImSwitch/issues).

## Explanatory Video on how to get started with ImSwitch
Duration: 3

https://www.youtube.com/watch?v=Om6GWZZ_0So

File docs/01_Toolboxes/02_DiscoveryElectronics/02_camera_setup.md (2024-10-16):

---
id: Camera Setup
title: openUC2 Camera Setup
---

**We provide Docker Containers for our 3 major camera manufacturers: https://github.com/openUC2/ImSwitchDockerInstall**

The openUC2 Camera Setup provides guidance on configuring and using webcams and Daheng cameras for imaging purposes within the openUC2 ecosystem. This setup allows users to seamlessly integrate cameras into their experimental setups and utilize them for imaging and data acquisition. Below are detailed instructions for setting up cameras on different platforms:

## Webcam

### On Windows
- Users can utilize the built-in webcam functionality provided by Windows. They need to open the webcam using the Windows internal software and start streaming.

### On Mac
- For Mac users, the Photobooth application can be used to access the webcam. Simply open the Photobooth application and select the camera to start capturing images or videos.

### Alternative Method
- Users can also use the openUC2 Web Serial interface available at `https://youseetoo.github.io/indexWebSerialTest.html` to open the camera stream.

## Daheng Cameras

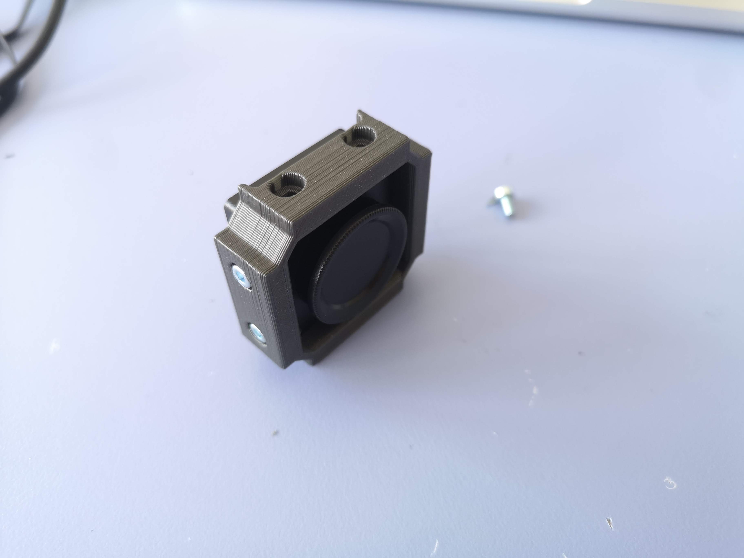
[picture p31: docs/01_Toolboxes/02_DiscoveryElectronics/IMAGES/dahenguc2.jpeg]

*This may look completely different now, but important: A camera is inside the cube :)*

### On Windows
- To use Daheng cameras on Windows, users should visit the [Get-camera supplier website](https://www.get-cameras.com/customerdownloads?submissionGuid=93704570-544a-43e8-83d6-f5f3cf0b97fb).
- From the provided options, select the "Windows SDK USB2+USB3+GigE (including Directshow + Python) Galaxy V1.23.2305.9161" package.
- Install the software and drivers from the downloaded package.
- Once installed, users can start the "Galaxy Viewer" application to begin capturing images using the Daheng camera.

### Using Jetson Nano with Docker
If you're using Jetson Nano for image acquisition, you can set up a Docker container:
**We provide Docker Containers for our 3 major camera manufacturers: https://github.com/openUC2/ImSwitchDockerInstall**

### On Linux (Mac not supported)

You can install the driver and test the frame acquistion using the following commands:

```bash
# We use Ubuntu
# Install necessary dependencies
sudo apt-get update && apt-get install -y \
    wget \
    unzip \
    python3 \
    python3-pip \
    usbutils \
    sudo \
    nano \
    git \
    expect

# Create the udev rules directory
sudo mkdir -p /etc/udev/rules.d

# Download and install the appropriate Hik driver based on architecture
cd /tmp && \
    wget https://dahengimaging.com/downloads/Galaxy_Linux_Python_2.0.2106.9041.tar_1.gz && \
    wget https://dahengimaging.com/downloads/Galaxy_Linux-armhf_Gige-U3_32bits-64bits_1.5.2303.9202.zip && \
    unzip Galaxy_Linux-armhf_Gige-U3_32bits-64bits_1.5.2303.9202.zip && \
    tar -zxvf Galaxy_Linux_Python_2.0.2106.9041.tar_1.gz && \
    cd Galaxy_Linux-armhf_Gige-U3_32bits-64bits_1.5.2303.9202 && \
    chmod +x Galaxy_camera.run && \
    cd /tmp/Galaxy_Linux_Python_2.0.2106.9041/api && \
    python3 setup.py build && \
    python3 setup.py install

# Run the installer script using expect to automate Enter key presses
echo "Y En Y" | /tmp/Galaxy_Linux-armhf_Gige-U3_32bits-64bits_1.5.2303.9202/Galaxy_camera.run

# Copy libgxiapi.so to /usr/lib and set the library path
cp /usr/lib/libgxiapi.so /usr/lib && \
    cp /tmp/Galaxy_Linux-armhf_Gige-U3_32bits-64bits_1.5.2303.9202/libgxiapi.so /usr/lib && \
    ldconfig

# Ensure the library path is set
LD_LIBRARY_PATH="/usr/lib:/tmp/Galaxy_Linux-armhf_Gige-U3_32bits-64bits_1.5.2303.9202:$LD_LIBRARY_PATH"

pip install pillow numpy
```

Then checkout the files under `/tmp/Galaxy_Linux_Python_2.0.2106.9041/`

### On Android Phones
- To use Daheng cameras on Android phones, users should first visit `https://www.get-cameras.com/customerdownloads?submissionGuid=93704570-544a-43e8-83d6-f5f3cf0b97fb`.
- From the provided options, select the "Android USB3 SDK v1.2.2112.9201" package and download it.
- After downloading, unzip the package and install the "GxViewer_GetRawImage.apk" on the Android phone (users may need to allow installation of apps from unknown sources or 3rd party apps).
- Connect the Daheng camera to the Android phone using a USB-C to Daheng cable (adapter).
- Open the installed app ("GxViewer_GetRawImage") and grant access to the USB connection when prompted.
- Users can adjust camera settings by swiping left in the app and then proceed to capture images.

Here is an extended documentation for the HIK camera setup:

## HIK Cameras

We use the MV-CS060-10UM/UC-PRO 600 with the IMX179 sensor.


*This may look completely different now, but important: A camera is inside the cube :)*
  
### On Windows
- Visit the [HIK supplier website](https://www.hikrobotics.com/en/support/download) for the latest software.
- Download the "MVS V2.1.2" package (or the latest version) for Windows.
- Install the software and drivers from the package.
- Use the "MVS Viewer" to capture and configure images with the HIK camera.

### On Linux (Ubuntu)
Install the HIK driver and run the camera with the following steps:

```bash
# Update system and install necessary dependencies
sudo apt-get update && sudo apt-get install -y \
    wget \
    unzip \
    python3 \
    python3-pip \
    usbutils

# Download and unzip the HIK driver package
cd /tmp && \
    wget https://www.hikrobotics.com/en/source/support/software/MVS_STD_GML_V2.1.2_231116.zip && \
    unzip MVS_STD_GML_V2.1.2_231116.zip

# Install the driver
sudo dpkg -i MVS-2.1.2_aarch64_20231116.deb

# Set up environment variables
export MVCAM_COMMON_RUNENV=/opt/MVS/lib
export LD_LIBRARY_PATH=/opt/MVS/lib/64:/opt/MVS/lib/32:$LD_LIBRARY_PATH

# Install Python dependencies
pip install pillow numpy

# Run the Python example to grab images
python3 /opt/MVS/Samples/aarch64/Python/MvImport/GrabImage.py
```

### Using Jetson Nano with Docker
If you're using Jetson Nano for image acquisition, you can set up a Docker container:
**We provide Docker Containers for our 3 major camera manufacturers: https://github.com/openUC2/ImSwitchDockerInstall**

This setup ensures that the HIK camera can be used on various platforms, providing flexibility across different devices.
## Video Tutorial
A video tutorial demonstrating the camera setup is available at `https://youtu.be/PtdU5qE6BSc`.

The openUC2 Camera Setup provides users with easy-to-follow instructions for configuring and utilizing webcams and Daheng cameras on different platforms, enabling seamless integration into various imaging applications and experiments.

<iframe width="560" height="315" src="https://www.youtube.com/embed/PtdU5qE6BSc" title="YouTube video player" frameborder="0" allow="accelerometer; autoplay; clipboard-write; encrypted-media; gyroscope; picture-in-picture; web-share" allowfullscreen></iframe>

## XIAO Sense Camera

Coming Soon.

You can have a glimpse here https://github.com/openUC2/openUC2-SEEED-XIAO-Camera/

and Here https://openuc2.github.io/docs/Toolboxes/DiscoveryElectronics/04_1_seeedmicroscope

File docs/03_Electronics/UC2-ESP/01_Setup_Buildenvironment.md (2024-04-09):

# UC2-ESP Firmware for the openUC2 UC2e electronics

:::info
This refers to the UC2-ESP firmware that can be found here: https://github.com/youseetoo/uc2-esp32
:::

This repository provides the latest (`V2`) firmware that controls external hardware like Motors, LEDs, Lasers and other customized elements using an ESP32 and an adapter board. It is inspired by the [UC2-REST](https://github.com/openUC2/UC2-REST/tree/master/ESP32) firmware, but features a much more structured way of the code by dividing modules into seperated classes. A `ModuleController` ensures a proper initializiation of individual modules at runtime, which makes the entire code very modular and follows the overall UC2 principle.

Similar to the legacy UC2-REST Firmware, the microcontroller can communicate using the wired serial and the wireless WiFi protocol. Both rely on a more-less similar `REST API` that uses endpoints to address an `act, get, set` command. For example, the information about the state of the ESP can be retrieved by issuing the code:

```
{"task":"/state_get"}
```

A list of all commands that can be sent via HTTP requests and serial commands (e.g. by using the Arduino IDE-contained Serial monitor at 50000 BAUD) can be found in the [RestApi.md](./RestApi.md)-file.

# Setting up the build environment

Certainly! Below is a tutorial crafted for beginners who are interested in developing firmware for the UC2-ESP project using Visual Studio Code with PlatformIO. This project is specifically designed for the ESP32 platform, leveraging both Arduino and ESP-IDF frameworks as defined in its `platformio.ini` file.

### Prerequisites
Before diving into the development process, ensure you have the following:
1. **Visual Studio Code** installed on your computer.
2. **PlatformIO IDE** extension for Visual Studio Code.
3. **Git** installed for cloning the repository.

### Setting Up Your Development Environment

#### Step 1: Install Visual Studio Code and PlatformIO
1. Download and install **Visual Studio Code** (VS Code) from the [official website](https://code.visualstudio.com/).
2. Open VS Code and navigate to the Extensions view by clicking on the square icon on the sidebar or pressing `Ctrl+Shift+X`.
3. Search for "PlatformIO IDE" and click on the install button.
4. Restart VS Code to ensure the PlatformIO IDE extension is properly loaded.

#### Step 2: Clone the UC2-ESP Repository
1. Open a terminal or command prompt.
2. Clone the UC2-ESP repository by executing:
   ```
   git clone --recurse-submodules https://github.com/youseetoo/uc2-esp32
   ```
3. This command clones the repository and all its submodules, ensuring you have the complete codebase.

#### Step 3: Open the Project in VS Code
1. Open VS Code, go to the File menu, and select "Open Folder".
2. Navigate to the directory where you cloned the UC2-ESP repository and select the `uc2-esp32` folder.

#### Step 4: Configuration
1. Once the project is open in VS Code, locate the `platformio.ini` file in the root directory. This file contains the configuration for your project environment.
2. If your development board is connected, you can set the `upload_port` based on your system:
   - For Linux/Mac: `upload_port = /dev/cu.SLAB_USBtoUART`
   - For Windows: `upload_port = COM3` (adjust the COM port based on your system)
3. Examine the `PinConfig.h` file to select the appropriate board configuration by setting the desired `PinConfig` structure, e.g., `const UC2_3 pinConfig;`.
4. Changing debug level: 
```
build_flags = 
	-DCORE_DEBUG_LEVEL=0
```
#### Step 5: Building and Uploading the Firmware
1. With the project open in VS Code, click on the PlatformIO icon on the sidebar.
2. Under the "Quick Access" section, locate your environment (e.g., `esp32dev`) and click on the "Upload" button. This action compiles the code and uploads it to your ESP32 board.
3. After uploading, the terminal will display messages about the process. A successful upload ends with "Leaving... Hard resetting via RTS pin...".

#### Step 6: Monitoring Output
1. To view the serial output from your ESP32, click on the "Monitor" button in the PlatformIO Quick Access section.
2. Ensure the `monitor_speed` in the `platformio.ini` file matches the baud rate set in your program (default is 500000 for this project).
3. If necessary, reset your ESP32 board to start the program from the beginning.

#### Step 7: Debugging and Troubleshooting
If you encounter issues during development or uploading:
- Double-check your `platformio.ini` configurations, especially the `upload_port` and board settings.
- Review the serial monitor output for any error messages.
- Ensure your ESP32 board is correctly connected to your computer.
- For specific problems, consider filing an issue in the [UC2-ESP GitHub repository](https://github.com/youseetoo/uc2-esp32) for support.

### Testing and Experimentation
To test various functionalities, refer to the `json_api_BD.txt` file in the `main` directory for a collection of JSON commands that can be sent to the ESP32.

This guide covers the basics to get started with firmware development for the UC2-ESP project using VS Code and PlatformIO. As you become more familiar with the project, explore the codebase to understand the implementation details and how you can contribute to its development.

In order to test several commands, you can find a useful list of `json`files in this file: [main/json_api_BD.txt](main/json_api_BD.txt)

# Flash the firmware using the Web-Tool

A new way to flash the firmware to the ESP32 is to use the open-source ESPHome Webtool. We have modified it such that the software in thi repo is compiled and uploaded to the website:

**[www.youseetoo.github.io]**(youseetoo.github.io)

There you can select the board you have and flash the code. If the driver is properly installed, you simply select the port and hit `start`. The firmware will automatically be downloaded and flashed through the browser.


*This shows the gui to first select the board you have before the browser (chrome/edge) automatically flashes the firmware.*

# Additional information

This is a fastly moving repo and the information may get outdated quickly. Please also check the relevant information in our [documentation](https://openuc2.github.io/docs/Electronics/uc2e1)

# Information about the REST commands

Every component can be used by calling it in a REST-ful way. A not-complete document that describes the most important functions can be found [here](./RestApi.md)

The general structure for the serial would become:

````
{"task": "/state_get"}
````

to get the information about the MCU. A additional cheat-sheet can be found [here](main/json_api_BD.txt)

# Some Arduino-CLI/ESPTOOL/PlatformIO-related commands

This is a random collection of tasks/commands that are useful to compile/upload the code by hand.

Convert the firmware into a single file:

```
cd uc2-ESP/.pio/build/esp32dev
python -m esptool --chip esp32 merge_bin  -o merged-firmware.bin  --flash_mode dio  --flash_freq 40m  --flash_size 4MB  0x1000 bootloader.bin  0x8000 partitions.bin  0xe000 boot_app0.bin  0x10000 firmware.bin
```

Install the ESP32 core

```
arduino-cli core update-index --config-file arduino-cli.yaml
arduino-cli core install esp32:esp32
arduino-cli board list
```

Compile the firmware in a dedicated output folder

```
mkdir build
arduino-cli compile --fqbn esp32:esp32:esp32:PSRAM=disabled,PartitionScheme=huge_app,CPUFreq=80 ESP32/main/main.ino  --output-dir ./build/ --libraries ./libraries/
```

Flash the firmware to the ESP32 board

```
esptool.py --chip esp32 --port /dev/cu.SLAB_USBtoUART --baud 921600 --before default_reset --after hard_reset write_flash -z --flash_mode dio --flash_freq 80m --flash_size 4MB 0x1000 /build/main.ino.bootloader.bin 0x8000 /build/main.ino.partitions.bin 0xe000 /build/boot_app0.bin 0x10000 /build/main.ino.bin
```

Upload the firmware using the Arduino-CLI

```
arduino-cli upload -p /dev/cu.usbserial-1310 --fqbn esp32:esp32:esp32-poe-iso .
```

Screen the serial monitor

```
screen /dev/cu.usbserial-1310 115200
```

Upload via esptool:

```
pip install esptool
python -m esptool --chip esp32 --port /dev/cu.SLAB_USBtoUART --baud 921600  write_flash --flash_mode dio --flash_size detect 0x0 main.ino.bin
```

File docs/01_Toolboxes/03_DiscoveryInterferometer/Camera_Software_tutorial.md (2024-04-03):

---
id: SoftwareTutorial
title: HIK-Camera Software Installation
---

### Install MVS App for Camera Utilization

Camera model: MV-CE060-10UC. Visit the HIKROBOTICS website and download the MVS software suitable for your computer. Below are steps exemplifying the software installation for Mac.

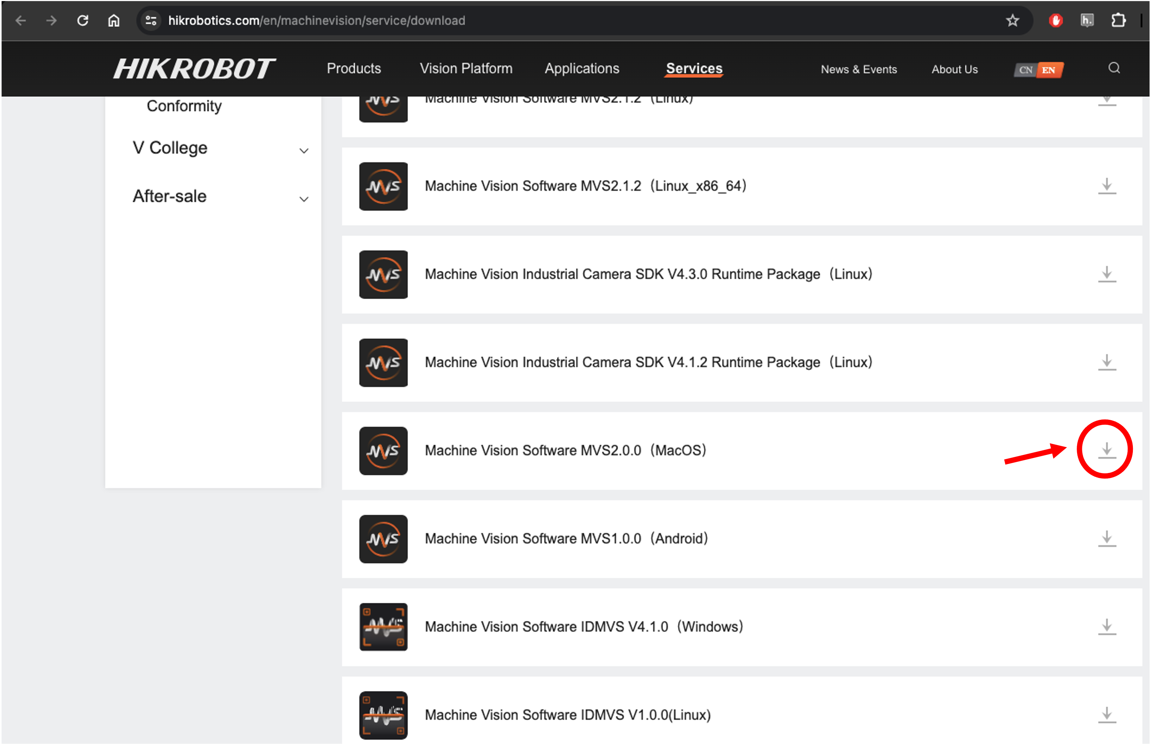
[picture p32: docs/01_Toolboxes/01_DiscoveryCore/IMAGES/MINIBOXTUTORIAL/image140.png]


Install the downloaded file.



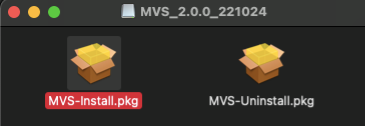
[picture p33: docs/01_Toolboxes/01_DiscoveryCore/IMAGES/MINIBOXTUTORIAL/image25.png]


Open the MVS Software.

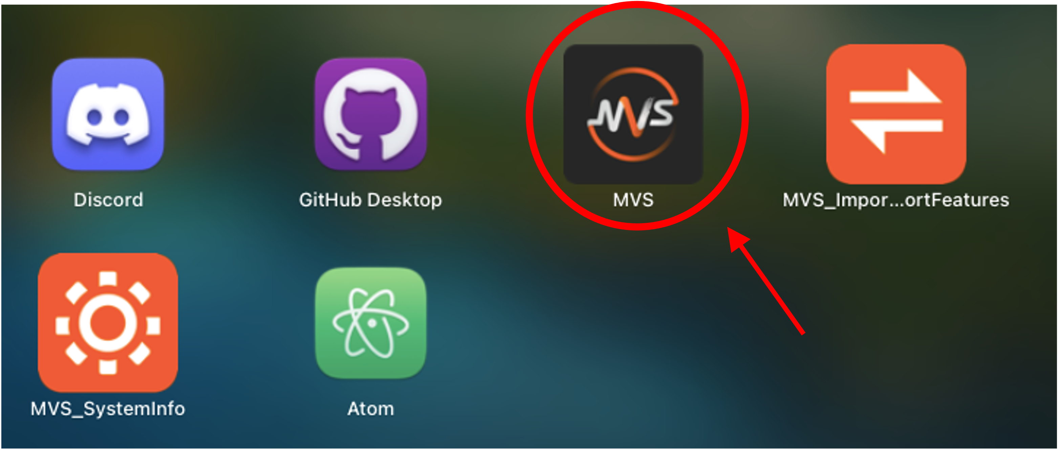
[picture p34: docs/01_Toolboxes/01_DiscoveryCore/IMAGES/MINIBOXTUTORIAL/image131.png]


You should see the following window.

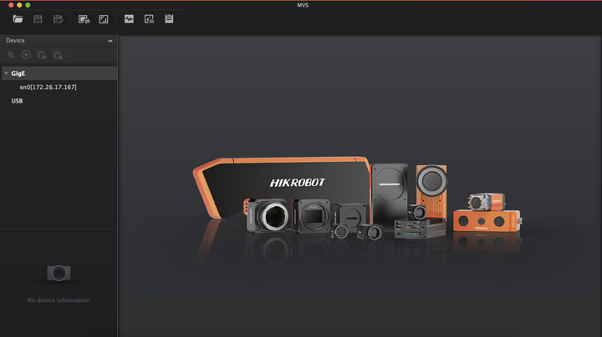
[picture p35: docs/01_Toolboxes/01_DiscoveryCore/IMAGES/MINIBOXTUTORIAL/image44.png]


Connect the camera. Refresh the USB line to detect the camera.

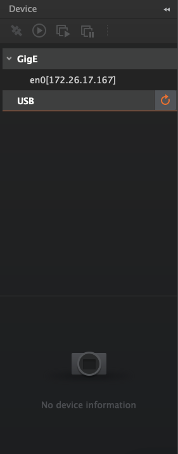
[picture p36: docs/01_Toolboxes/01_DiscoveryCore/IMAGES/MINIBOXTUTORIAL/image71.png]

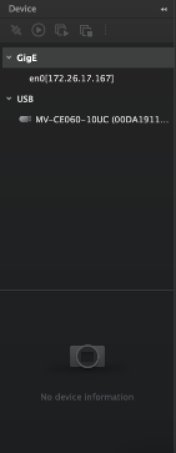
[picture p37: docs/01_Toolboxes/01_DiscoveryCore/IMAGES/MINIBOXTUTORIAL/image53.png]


Select the make-link button on the detected camera.

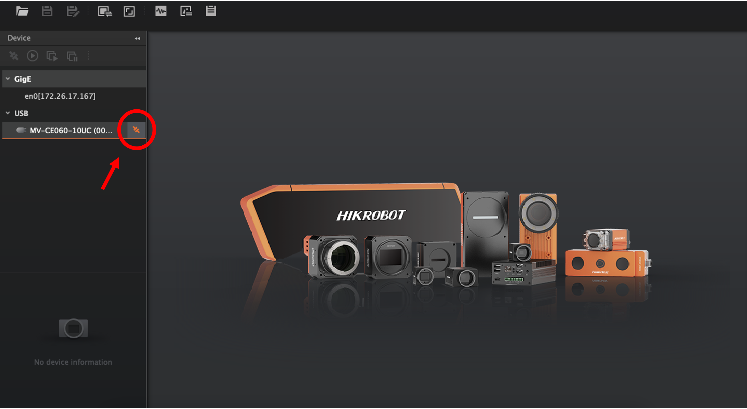
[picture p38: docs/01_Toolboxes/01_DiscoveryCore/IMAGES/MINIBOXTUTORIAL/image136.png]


The following window should be displayed.

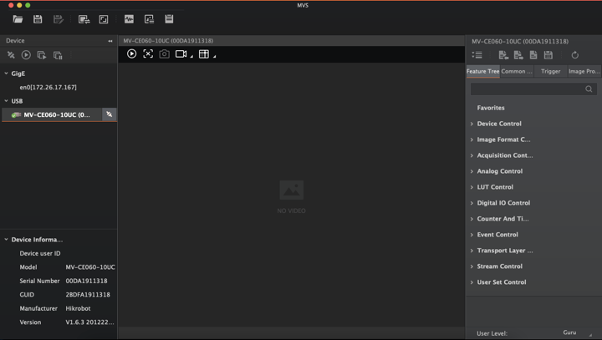
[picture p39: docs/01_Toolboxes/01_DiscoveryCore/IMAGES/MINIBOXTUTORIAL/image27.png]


Click on the play button in the actions bar of the camera.

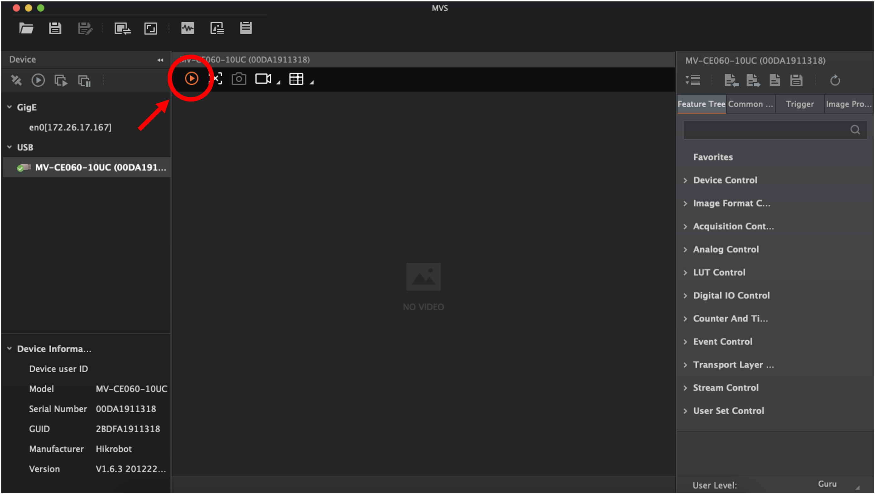
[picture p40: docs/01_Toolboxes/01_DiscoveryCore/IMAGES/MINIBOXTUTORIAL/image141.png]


If properly connected, you should see a real-time image. Adjust the exposure if the image is overexposed.

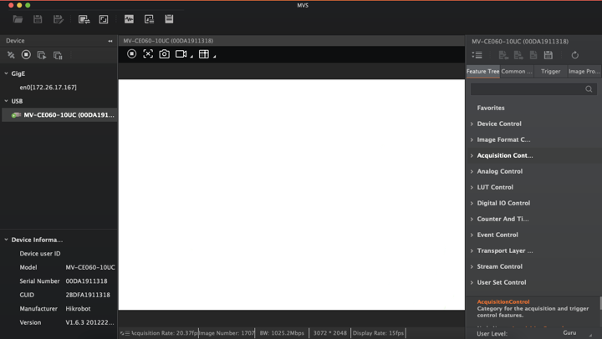
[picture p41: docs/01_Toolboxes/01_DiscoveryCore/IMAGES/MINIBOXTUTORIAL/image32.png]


To adjust the exposure time, go to the Feature tree, select the Acquisition Control Category, and change the Exposure Auto option to *Continuous*.

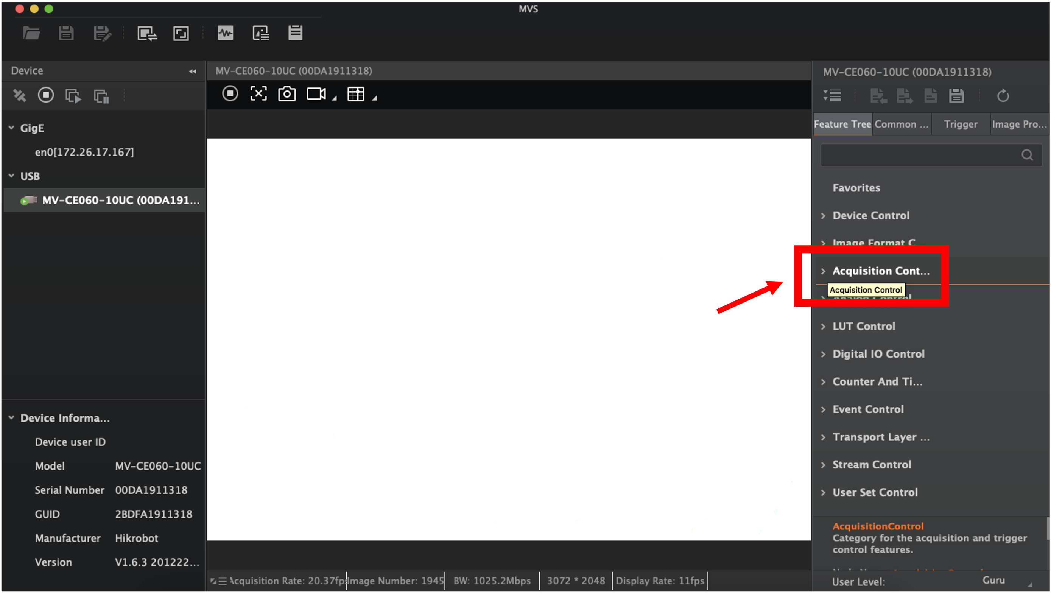
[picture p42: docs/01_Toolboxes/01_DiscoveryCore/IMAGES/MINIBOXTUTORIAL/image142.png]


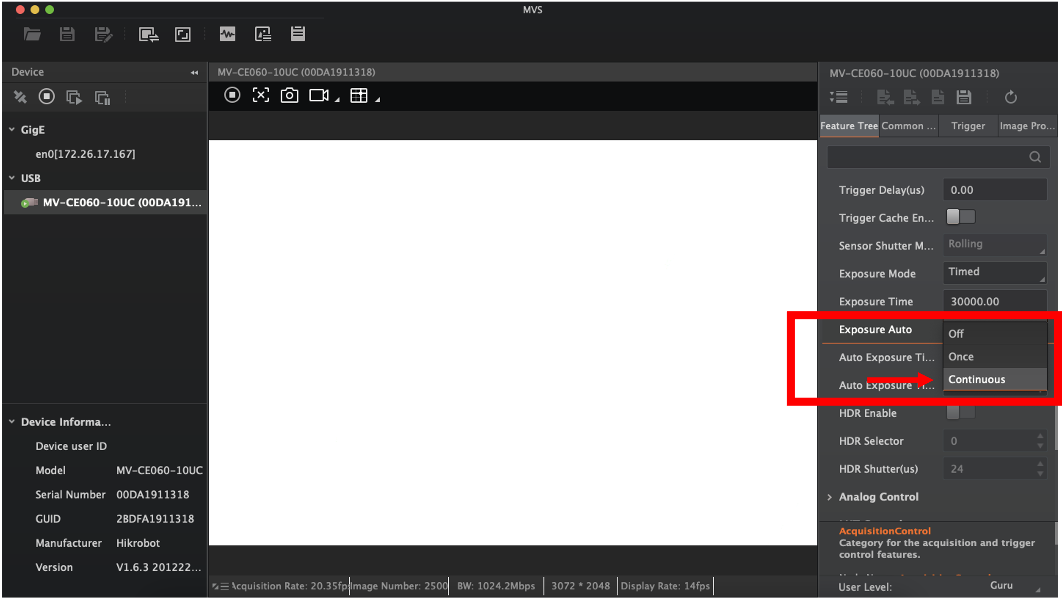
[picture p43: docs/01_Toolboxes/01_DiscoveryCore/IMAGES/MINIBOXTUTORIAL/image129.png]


Now, a clear image with good contrast should be visible.

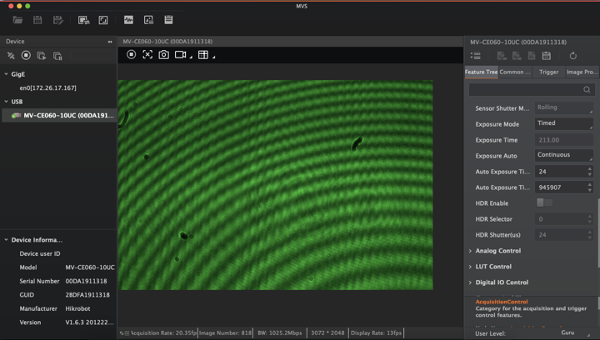
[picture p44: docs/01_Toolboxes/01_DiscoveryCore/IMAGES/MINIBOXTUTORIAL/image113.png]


To stop recording, click on the stop button in the camera's actions bar.

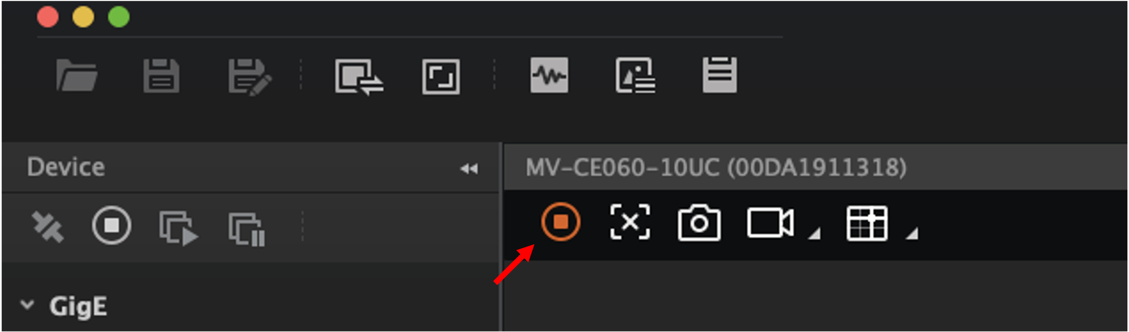
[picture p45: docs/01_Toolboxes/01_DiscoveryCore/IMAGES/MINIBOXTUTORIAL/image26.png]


To disconnect the camera, click on the break-link button next to the detected camera in the USB devices list.

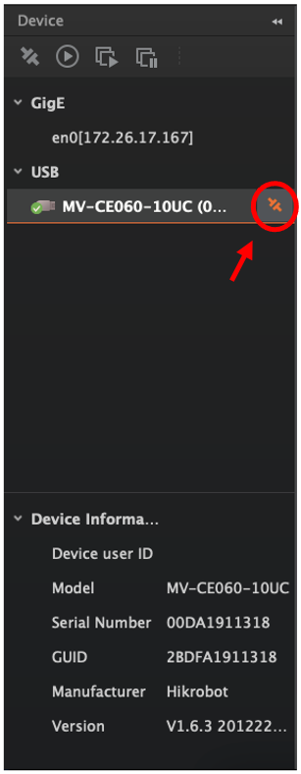
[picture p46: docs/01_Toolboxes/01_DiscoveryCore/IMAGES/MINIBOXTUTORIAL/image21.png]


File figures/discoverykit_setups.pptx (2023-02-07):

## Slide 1

1

2

3

4

50mm

5

50mm

6

100mm

11

7

8

12..14

9

25mm

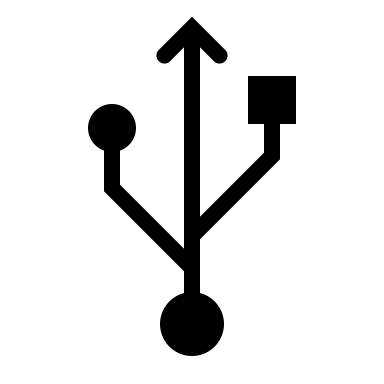
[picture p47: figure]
Stecker mit einfarbiger Füllung

UC2e

15

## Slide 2

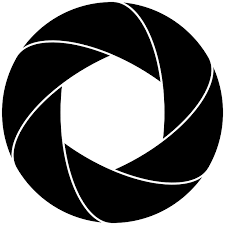
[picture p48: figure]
Aperture Photographer Taking - Free vector graphic on Pixabay
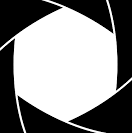
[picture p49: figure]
Aperture Photographer Taking - Free vector graphic on Pixabay

UC2e

50mm

50mm

100mm

25mm

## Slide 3

## Discovery Kit (Base)

## Incubator Microscope

## XY Stage Scanning Micrsocope

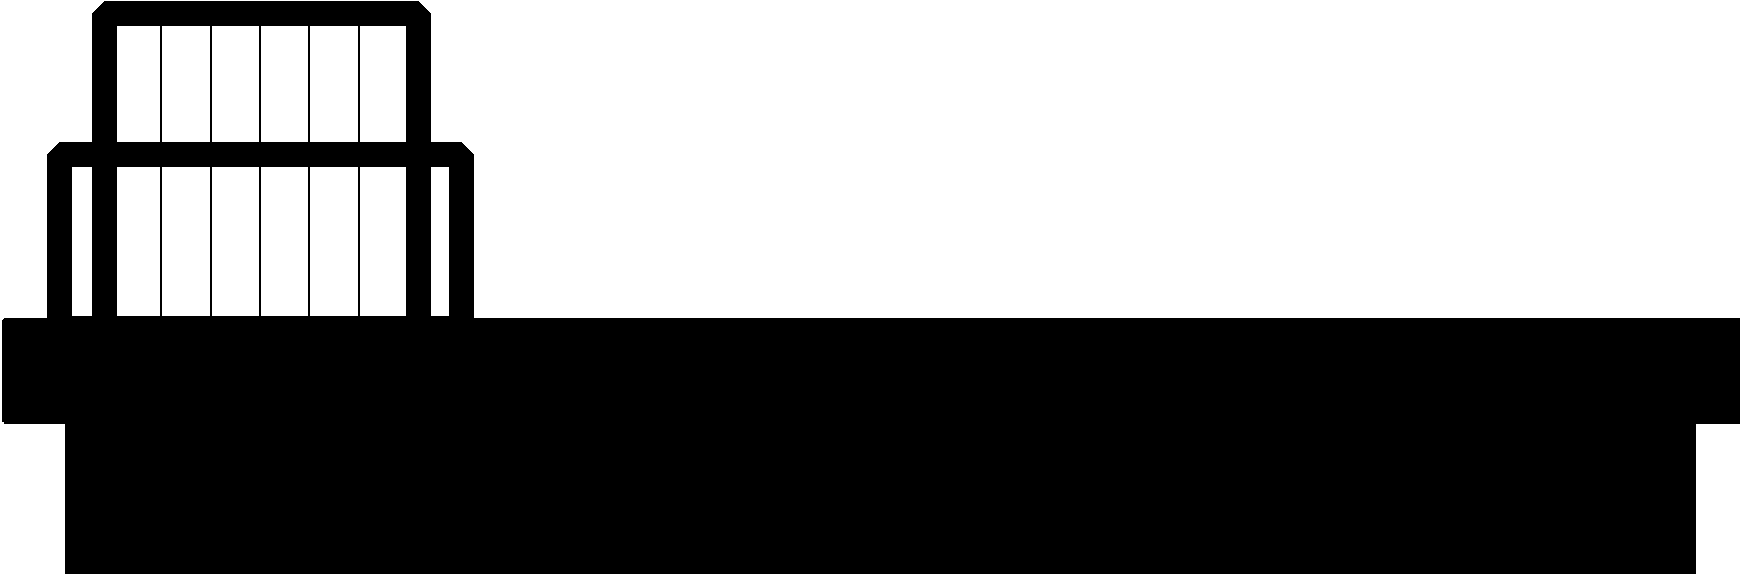
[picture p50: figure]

## Light-sheet Microscope

## Projector

## Phase Contrast Methods

## Smartphone Microscope

## Telescope

## Infinity corrected microscope

100mm

## Measure focal length of lens

## Discovery Extension Kit: Fourier

## Infinity corrected microscope BFP manipulation

100mm

50mm

50mm

## Fourier / Abbe Experiment

50mm

100mm

50mm

25mm

## Inline Holography

## Diffraction at a knife edge

## Discovery Extension Kit: Interferometry

## Beamexpander

## Diffraction: Double / Single Slit + Grating

## Spatial filtering

## Inline Holography

## Michelson Interferometer

## Motorized Michelson Interferometer

## Mach Zehnder Interferometer

## Off-Axis Holography

## Discovery Extension Kit: Fluorescence

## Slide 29

## Fluorescence Microscope

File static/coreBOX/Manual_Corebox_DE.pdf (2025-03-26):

# CoreBOX

## UC2 Handbuch

openUC2
GmbHHans-Knöll-Str. 6
07745 Jena, Germany
E-Mail: hello@openuc2.com
Webseite: www.openuc2.com

Handbuch-Version: 0.1 – März 2025
Schnellanleitung zur ersten Nutzung

Lesen Sie zuerst sorgfältig die Sicherheitshinweise.
Stellen Sie sicher, dass die Montage auf einer ebenen, stabilen Oberfläche erfolgt. Besuchen Sie openuc2.github.io oder forum. openuc2.com, um detaillierte Montage- und Nutzungshinweise zu erhalten.
Rechtliche Informationen

Dieses Handbuch enthält wichtige Informationen zur sicheren und korrekten Nutzung Ihres openUC2-Produkts. Bitte beachten Sie, dass Nichtbeachtung der hierin enthaltenen Anweisungen zu Schäden am Produkt, persönlicher Verletzung oder eingeschränkter Leistung führen kann. Die openUC2 GmbH übernimmt keinerlei Haftung für Schäden, die durch Missbrauch, unsachgemäße Handhabung oder Nichtbeachtung der Handbuchinformationen verursacht werden.

Herstellerkontakt:
openUC2 GmbH
Hans-Knöll-Str. 6
07745 Jena
Germany
E-Mail: hello@openuc2.com
Web: www.openuc2.com

Ausführliche Online-Dokumentation:
Deutsch: https://openuc2.github.io/docs/Toolboxes/DiscoveryCore/GERMAN/uc2miniboxDE
Englisch: https://openuc2.github.io/docs/Toolboxes/DiscoveryCore/ENGLISH/uc2miniboxEN
Support
Bei Fragen, Problemen oder Unklarheiten überprüfen Sie zuerst die letzten Kapitel dieses Handbuchs oder besuchen Sie unsere Support-Website unter support.openuc2.com für eine vollständige Liste häufig gestellter Fragen, Fehlerbehebungen und detaillierte Anleitungen. Weitere Unterstützung erhalten Sie im Community-Forum unter forum.openuc2.com oder per E-Mail unter hello@ openuc2.com.
Sicherheitshinweise

Verwenden Sie das Gerät stets gemäß den Anweisungen in diesem Handbuch. Trennen Sie das Gerät unbedingt von der Stromversorgung, bevor Sie Wartungsarbeiten durchführen. Stellen Sie das Gerät stets auf einer stabilen Oberfläche auf, um Kippen oder Herunterfallen zu verhindern.
Optische Komponenten können empfindlich sein; gehen Sie sorgsam mit Spiegeln, Linsen und anderen zerbrechlichen Teilen um, um Verletzungen zu vermeiden.

Achten Sie auf Kleinteile und Magnete, die von Kindern verschluckt werden könnten. Halten Sie diese von Kindern fern.
Bei beschädigten Teilen kontaktieren Sie umgehend unseren Support unter support.openuc2.com.
Sorgen Sie für ausreichende Belüftung bei der Nutzung optischer Komponenten, insbesondere bei LED- oder Laser-basierten Modulen.

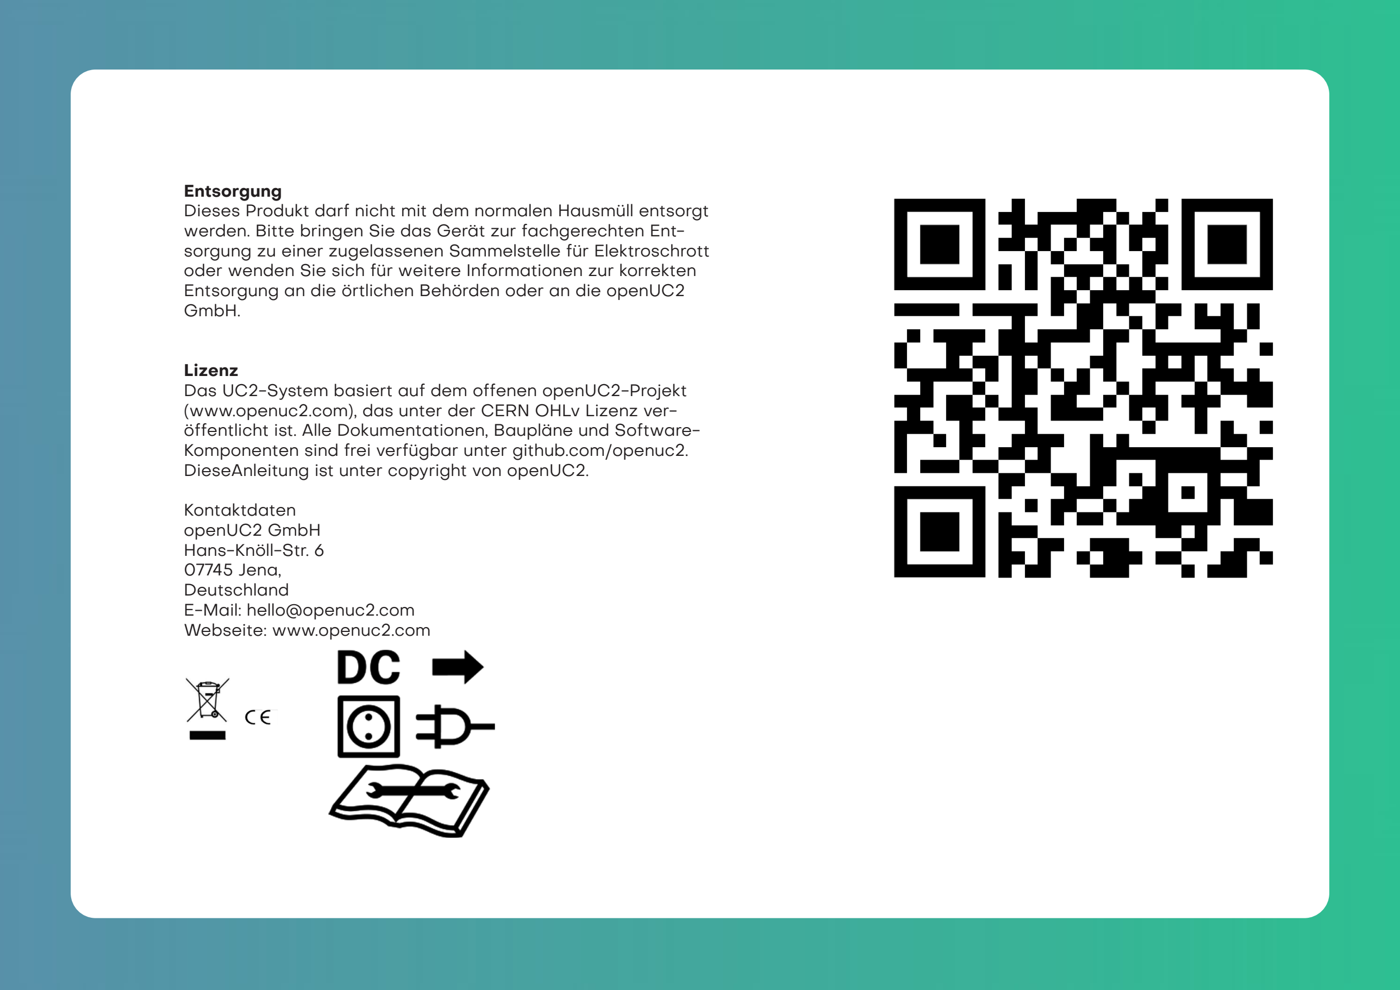
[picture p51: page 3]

Entsorgung
Dieses Produkt darf nicht mit dem normalen Hausmüll entsorgt werden. Bitte bringen Sie das Gerät zur fachgerechten Entsorgung zu einer zugelassenen Sammelstelle für Elektroschrott oder wenden Sie sich für weitere Informationen zur korrekten Entsorgung an die örtlichen Behörden oder an die openUC2 GmbH.

Lizenz
Das UC2-System basiert auf dem offenen openUC2-Projekt (www.openuc2.com), das unter der CERN OHLv Lizenz veröffentlicht ist. Alle Dokumentationen, Baupläne und Software-Komponenten sind frei verfügbar unter github.com/openuc2. DieseAnleitung ist unter copyright von openUC2.

Kontaktdaten
openUC2 GmbH
Hans-Knöll-Str. 6
07745 Jena,
Deutschland
E-Mail: hello@openuc2.com
Webseite: www.openuc2.com

# Inhalt der CoreBOX

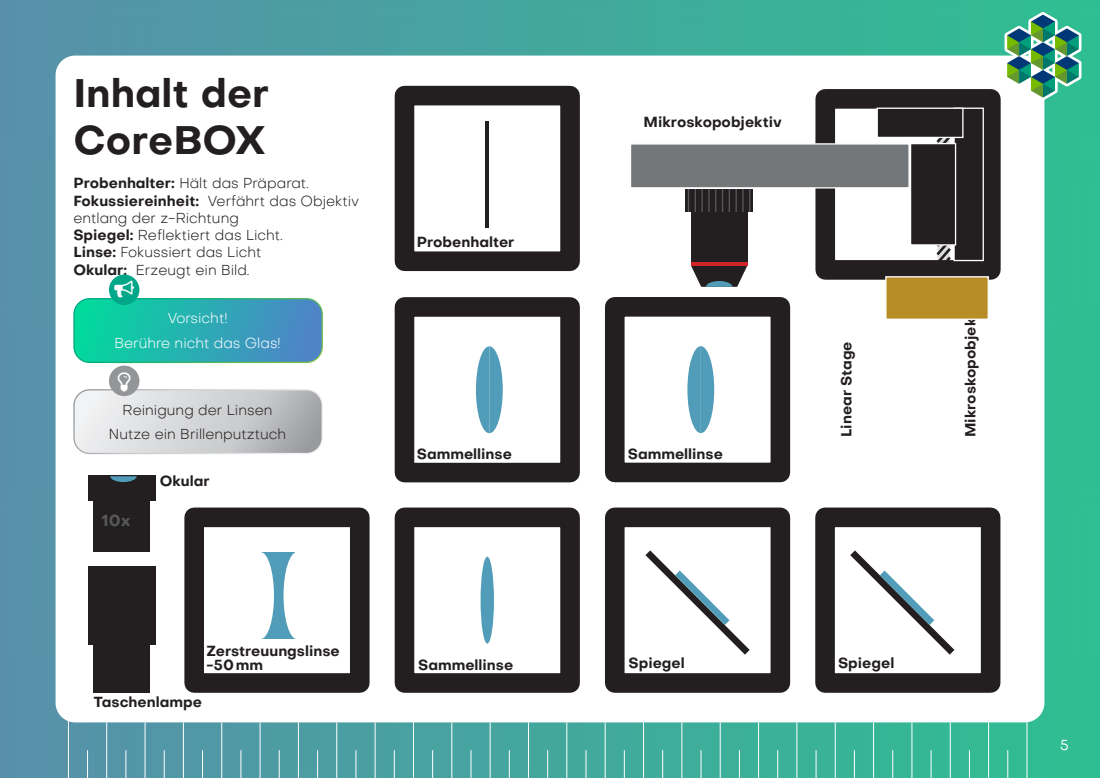
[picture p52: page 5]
Sammellinse; Probenhalter; Spiegel; Spiegel Zerstreuungslinse; Linear Stage; Mikroskopobjektiv; Okular; Taschenlampe

Probenhalter: Hält das Präparat.
Fokussiereinheit: Verfährt das Objektiv
entlang der z-Richtung
Spiegel: Reflektiert das Licht.
Linse: Fokussiert das Licht
Okular: Erzeugt ein Bild.
Vorsicht!
Berühre nicht das Glas!
Reinigung der Linsen
Nutze ein Brillenputztuch

Würfel

Würfel (Hälfte)

Einsatz (z.B. Probenhalter)

Würfel (Hälfte)

Grundplatte

# You.See.Too.? UC2!

Das Kernelement des UC2-Projekts ist ein einfacher Würfel. Der Würfel besteht aus zwei Hälften und beherbergt einen verschiebbaren Einsatz. Der Einsatz kann verschiedene optische Komponenten (z.B. Linsen, Spiegel) halten, womit sich mit jedem Würfel unteschiedliche Funktionen realisieren lassen. Die Würfel, sowie die in alle Richtungen erweiterbaren Grundplatten im Puzzleformat sind Spritzgegossen und haben dadurch eine hohe Präzision. Gehalten werden die Teile per Formschluss, was die Nutzung von Magneten und Schrauben erübrigt. Die Einsätze im Stopschildformat lassen sich schnell an neue Komponenten anpassen und finden im Würfel platz.

# Würfeltyp 1

Spritzguss mit Steckverbindung

Der Würfel lässt sich auf eine Grundplatte montieren. Die Grundplattenmodule lassen sich wie Puzzle zusammenstecken.

Grundplatte

Grundplatte mit Magneten

# UC2 zum Selberdrucken

Neben dem spritzgussfähigen Design kommt der Würfel auch in einer druckbaren Version daher. Beide Würfel sind miteinander kompatibel, jedoch lässt sich der Würfel bestehend aus Deckel und Korpus besser drucken. Die magnetischen Schrauben dienen dazu, sich mit den Kugelmagneten auf der Platte zu verbinden. Durch die Kombination verschiedener Würfelmodule lassen sich ganz einfach verschiedene optische Aufbauten zusammenbauen. Mit jedem Würfel kann eine neue Funktion hinzugefügt werden. Deiner Kreativität sind keine Grenzen gesetzt.

# Würfeltyp 2

3D gedruckt mit Magnetverbindung

Grundplatte

Würfel

Würfel (Körper)

Schrauben (magnetisch)

Kugelmagnete

Würfel (Deckel)

In der 3D-gedruckten Grundplatte sind kleine Kugelmagnete eingelassen, auf die die Würfel gesteckt
werden.
Willst du mehr Würfel haben? Dann kannst du
sie selbst bauen. Du findest alles hier.

# So passen die Würfel zusammen

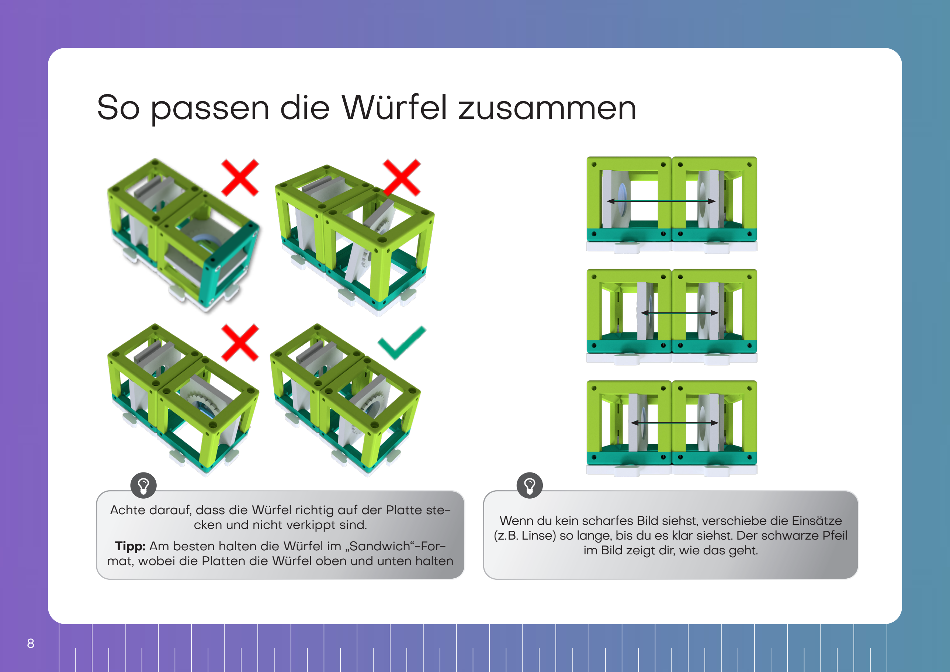
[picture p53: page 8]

Achte darauf, dass die Würfel richtig auf der Platte stecken und nicht verkippt sind. Tipp: Am besten halten die Würfel im „Sandwich“-Format, wobei die Platten die Würfel oben und unten halten

Wenn du kein scharfes Bild siehst, verschiebe die Einsätze (z.B. Linse) so lange, bis du es klar siehst. Der schwarze Pfeil im Bild zeigt dir, wie das geht.

# Das kann eine Linse

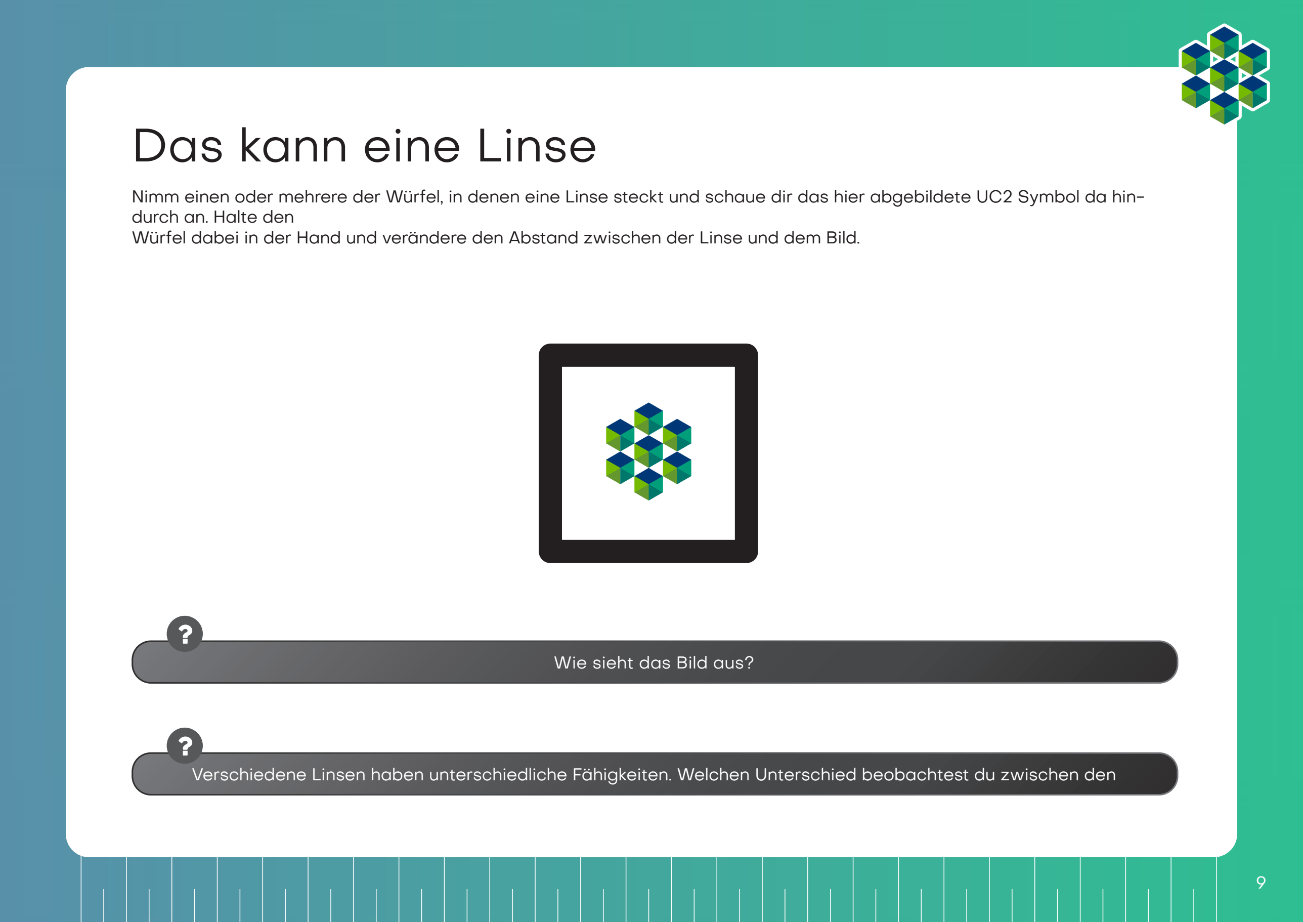
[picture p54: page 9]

Nimm einen oder mehrere der Würfel, in denen eine Linse steckt und schaue dir das hier abgebildete UC2 Symbol da hindurch an. Halte den
Würfel dabei in der Hand und verändere den Abstand zwischen der Linse und dem Bild.

Verschiedene Linsen haben unterschiedliche Fähigkeiten. Welchen Unterschied beobachtest du zwischen den

Wie sieht das Bild aus?

# Linsen

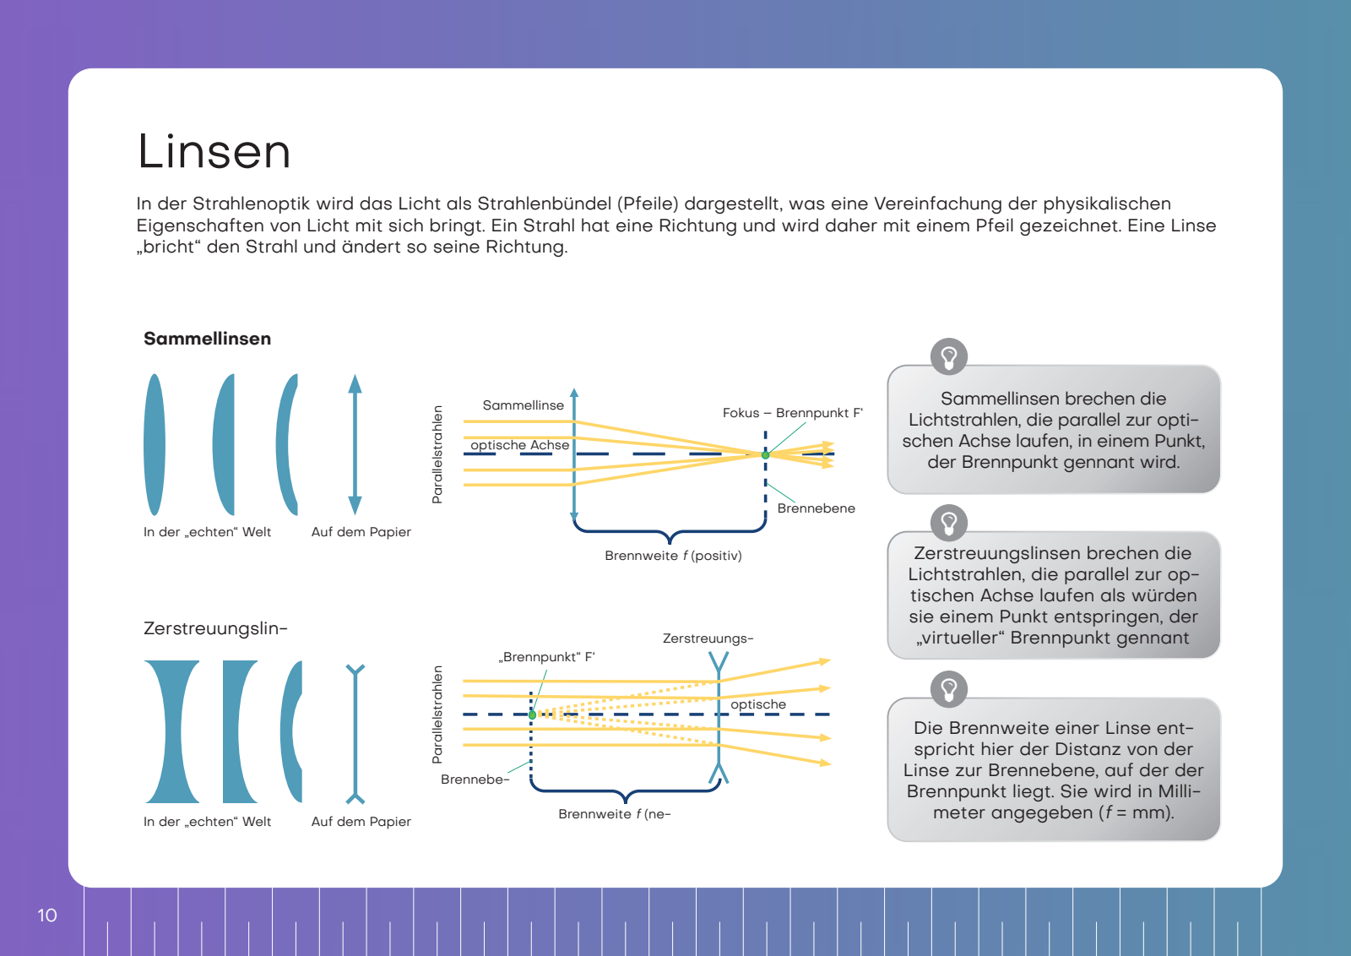
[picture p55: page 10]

In der Strahlenoptik wird das Licht als Strahlenbündel (Pfeile) dargestellt, was eine Vereinfachung der physikalischen Eigenschaften von Licht mit sich bringt. Ein Strahl hat eine Richtung und wird daher mit einem Pfeil gezeichnet. Eine Linse „bricht“ den Strahl und ändert so seine Richtung.

Sammellinsen brechen die
Lichtstrahlen, die parallel zur optischen Achse laufen, in einem Punkt, der Brennpunkt gennant wird.

Zerstreuungslinsen brechen die Lichtstrahlen, die parallel zur optischen Achse laufen als würden sie einem Punkt entspringen, der „virtueller“ Brennpunkt gennant

Die Brennweite einer Linse entspricht hier der Distanz von der Linse zur Brennebene, auf der der Brennpunkt liegt. Sie wird in Millimeter angegeben (f = mm).

Sammellinsen

In der „echten“ Welt Auf dem Papier

Fokus – Brennpunkt F‘ Sammellinse

Brennebene

Brennweite f (positiv)

Parallelstrahlen

optische Achse

Parallelstrahlen

„Brennpunkt“ F‘

Brennebe-

Brennweite f (ne-

Zerstreuungs-

optische

Zerstreuungslin-

In der „echten“ Welt Auf dem Papier

# Linsen „brechen“ die Lichtstrahlen

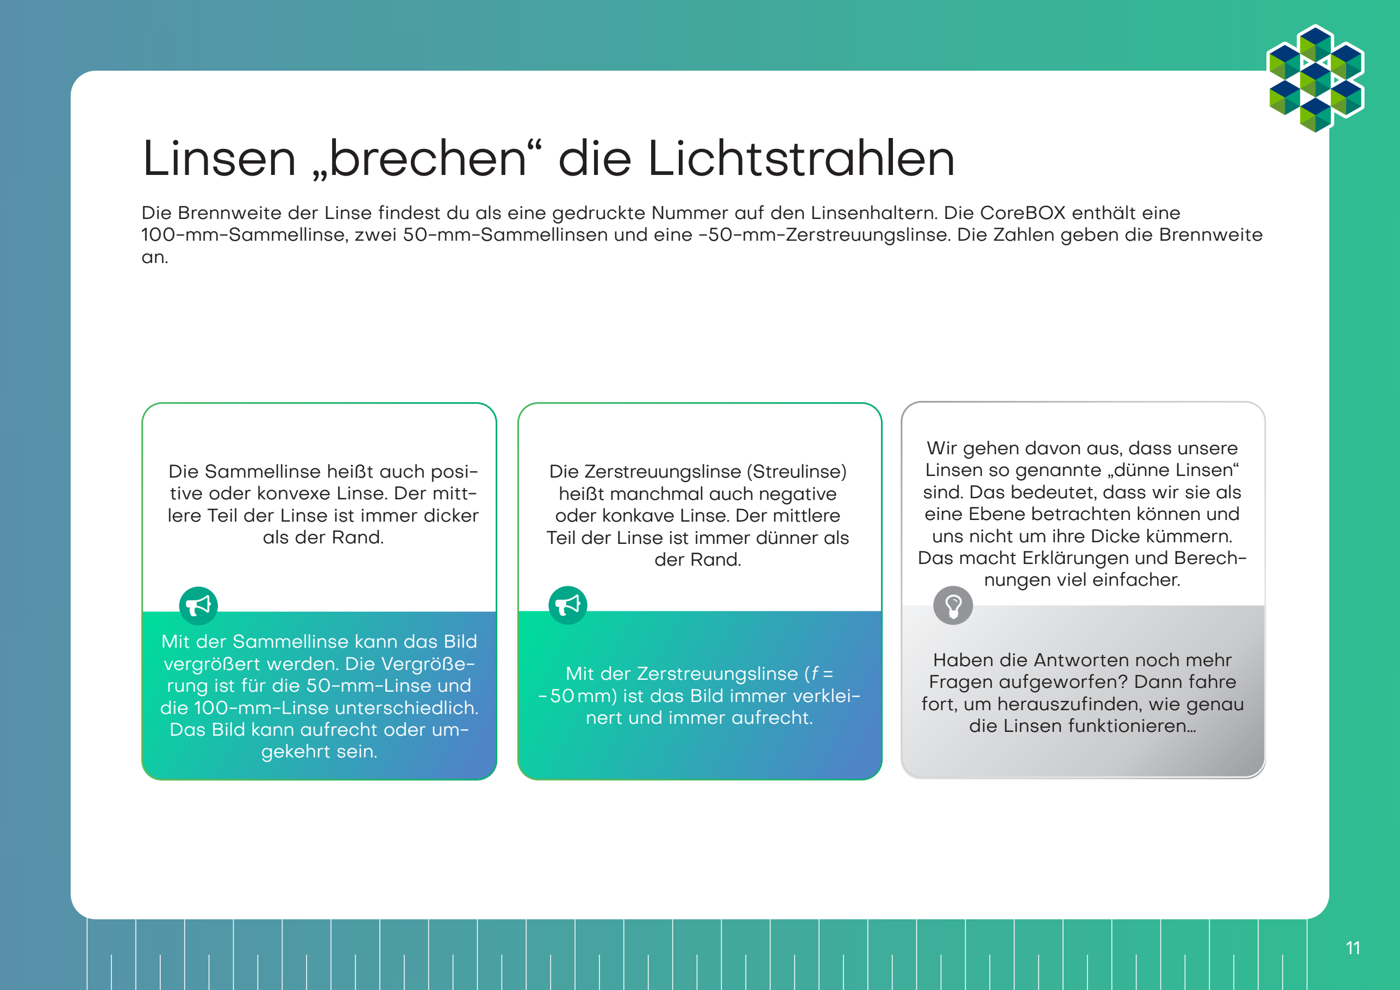
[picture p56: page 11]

Mit der Zerstreuungslinse (f = −50mm) ist das Bild immer verkleinert und immer aufrecht.

Haben die Antworten noch mehr Fragen aufgeworfen? Dann fahre fort, um herauszufinden, wie genau die Linsen funktionieren…

Wir gehen davon aus, dass unsere Linsen so genannte „dünne Linsen“ sind. Das bedeutet, dass wir sie als eine Ebene betrachten können und uns nicht um ihre Dicke kümmern. Das macht Erklärungen und Berechnungen viel einfacher.

Die Zerstreuungslinse (Streulinse) heißt manchmal auch negative oder konkave Linse. Der mittlere Teil der Linse ist immer dünner als der Rand.

Mit der Sammellinse kann das Bild vergrößert werden. Die Vergrößerung ist für die 50-mm-Linse und die 100-mm-Linse unterschiedlich. Das Bild kann aufrecht oder umgekehrt sein.

Die Sammellinse heißt auch positive oder konvexe Linse. Der mittlere Teil der Linse ist immer dicker als der Rand.

Die Brennweite der Linse findest du als eine gedruckte Nummer auf den Linsenhaltern. Die CoreBOX enthält eine 100-mm-Sammellinse, zwei 50-mm-Sammellinsen und eine -50-mm-Zerstreuungslinse. Die Zahlen geben die Brennweite an.

# Linsen-Abbildung

Nimm jetzt die Linsen-Würfel zur Hand. Versuche, mit der passenden Linse die jeweilige Angabe über die Brennweite in den abgebildeten Würfeln zu entziffern. Bewege die Linse über der Schrift bis sie die gleiche Größe hat wie der Text „UC2“ in der Mitte.

UC2

Was passiert, wenn du eine Linse mit der falschen Brennweite verwendest?

Kannst du den Text in der gleichen Größe und Ausrichtung wie das „UC2“ sehen? Was passiert, wenn du den Abstand zwischen der Linse und dem Bild veränderst?

f = +100mm

# f = -50mm

# Abbildung eines Gegenstandes durch eine positive Linse

Als Beispiel nehmen wir die Sammellinse. Wir starten mit einem Gegenstand (grüner Pfeil) und schauen, was mit den Strahlen passiert, die von der Spitze aus starten. Es gibt unendlich viele Strahlen in alle Richtung, für das Zeichnen der Abbildung reichen uns aber die drei folgenden Strahlen:
1. Der Mittelpunktstrahl (orange) geht ungestört durch das Zentrum der Linse.
2. Der Brennpunktstrahl (gelb) startet auch von der Spitze des Pfeils, geht aber durch den objektseitigen Brennpunkt in der Brennweite f. Nach der Linse verläuft er auf gleicher Höhe weiter, aber nun parallel zur optischen Achse.
3. Der Parallelstrahl (rot) läuft zunächst parallel zur optischen Achse, wird dann aber an der Linse so gebrochen, dass er durch den bildseitigen Brennpunkt in der Brennweite f verläuft.
Das Bild entsteht dort, wo sich alle Strahlen schneiden. Das Prinzip ist für alle Punkte bzw. die davon ausgehenden Strahlen eines Objekts gleich. Je nach dem, welche Linse benutzt wird und je nach Position des Objekts, verändern sich die Eigenschaften des Bildes, die Größe, die Orientierung und die Position.
Brennweite | Brennweite

Parallelstrahl

Brennebene | Brennebene

optische Achse

Brennpunktlstrahl

Bild

Linse

Mittelpunktstrahl

Gegenstand

# Abbildung eines Gegenstandes durch eine negative Linse

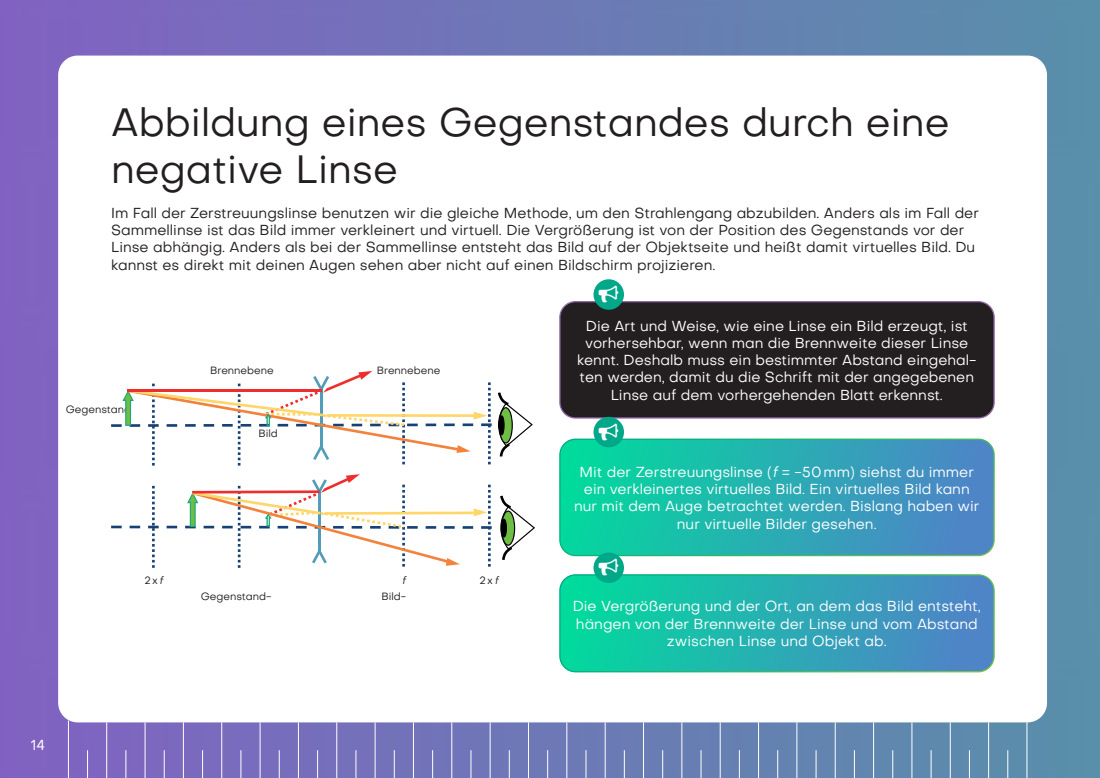
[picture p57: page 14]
Bild; Brennebene; Gegenstand; Gegenstand-; Bild-

Im Fall der Zerstreuungslinse benutzen wir die gleiche Methode, um den Strahlengang abzubilden. Anders als im Fall der
Sammellinse ist das Bild immer verkleinert und virtuell. Die Vergrößerung ist von der Position des Gegenstands vor der
Linse abhängig. Anders als bei der Sammellinse entsteht das Bild auf der Objektseite und heißt damit virtuelles Bild. Du
kannst es direkt mit deinen Augen sehen aber nicht auf einen Bildschirm projizieren.

Die Art und Weise, wie eine Linse ein Bild erzeugt, ist
vorhersehbar, wenn man die Brennweite dieser Linse
kennt. Deshalb muss ein bestimmter Abstand eingehal-
ten werden, damit du die Schrift mit der angegebenen
Linse auf dem vorhergehenden Blatt erkennst.

Mit der Zerstreuungslinse (f = -50mm) siehst du immer
ein verkleinertes virtuelles Bild. Ein virtuelles Bild kann
nur mit dem Auge betrachtet werden. Bislang haben wir

nur virtuelle Bilder gesehen.

Die Vergrößerung und der Ort, an dem das Bild entsteht,
hängen von der Brennweite der Linse und vom Abstand

zwischen Linse und Objekt ab.

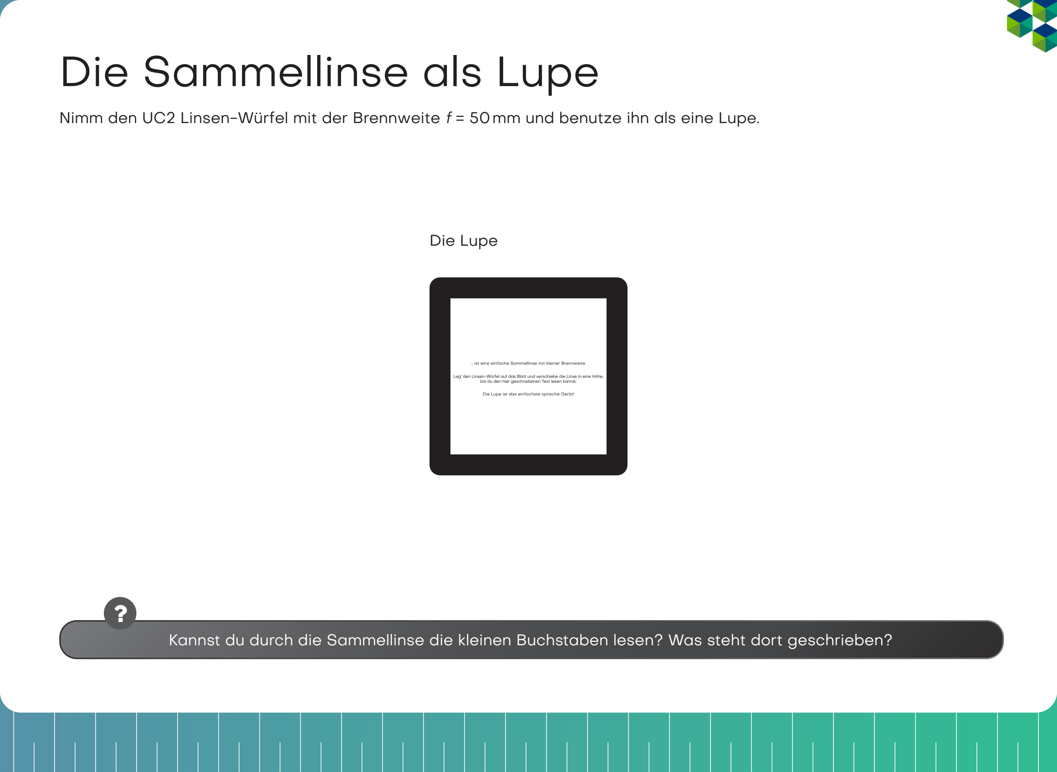
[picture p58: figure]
Die Sammellinse als Lupe; Die Lupe

Nimm den UC2 Linsen-Würfel mit der Brennweite f = 50mm und benutze ihn als eine Lupe.

… ist eine einfache Sammellinse mit kleiner Brennweite.

Leg‘ den Linsen-Würfel auf das Blatt und verschiebe die Linse in eine Höhe, bis du den hier geschriebenen Text lesen kannst.

Die Lupe ist das einfachste optische Gerät!

Kannst du durch die Sammellinse die kleinen Buchstaben lesen? Was steht dort geschrieben?

# Das machen Sammellinsen

Von den Sammellinsen hängt die Vergrößerung und Position des Gegenstands ab.

Wenn der Abstand zwischen Objekt und Linse
mehr als dem doppelten der Brennweite der
Linse entspricht, dann ist das Bild …
• umgekehrt
• seitenvertauscht
• verkleinert
• reell
genau der doppelten Brennweite der Linse
entspricht, dann ist das Bild …
Bild
• gleich groß
mehr als die Brennweite und weniger als dem
doppelten der Brennweite der Linse entspricht,
dann ist das Bild …
• vergrößert

Bildweite (b)
Der Abstand zwischen der
Linsenebene und dem von
der Linse erzeugten Bild
wird als b bezeichnet.

Gegenstandsweite (g)
Der Abstand zwischen
dem Objekt und der Lin-
senebene wird als g be-

Die Sammellinse kann ein
reelles Bild erzeugen. Das
reelle Bild sieht man dann
auf einem Bildschirm.

# Darum vergrößert die Lupe

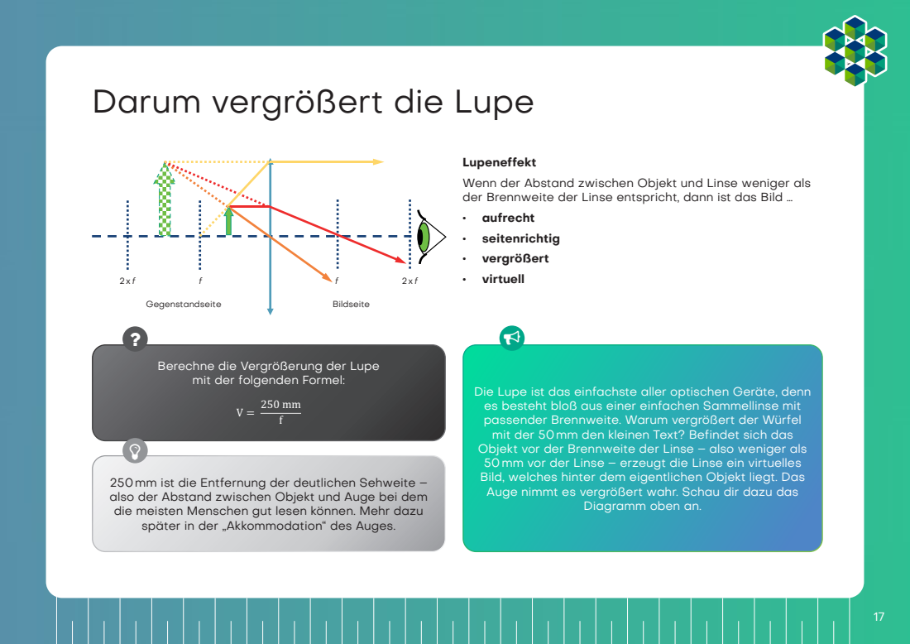
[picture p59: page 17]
Gegenstandseite; Bildseite

Lupeneffekt
Wenn der Abstand zwischen Objekt und Linse weniger als
der Brennweite der Linse entspricht, dann ist das Bild …
• aufrecht
• seitenrichtig
• vergrößert
• virtuell

Berechne die Vergrößerung der Lupe
mit der folgenden Formel:

Die Lupe ist das einfachste aller optischen Geräte, denn
es besteht bloß aus einer einfachen Sammellinse mit
passender Brennweite. Warum vergrößert der Würfel
mit der 50mm den kleinen Text? Befindet sich das
Objekt vor der Brennweite der Linse – also weniger als
50mm vor der Linse – erzeugt die Linse ein virtuelles
Bild, welches hinter dem eigentlichen Objekt liegt. Das
Auge nimmt es vergrößert wahr. Schau dir dazu das

250mm ist die Entfernung der deutlichen Sehweite –
also der Abstand zwischen Objekt und Auge bei dem
die meisten Menschen gut lesen können. Mehr dazu
später in der „Akkommodation“ des Auges.

Diagramm oben an.

# So funktioniert ein Kinoprojektor

Nimm dir den UC2-Linsenwürfel mit der Brennweite f = 50mm und platziere ihn hinter den Probenhalterwürfel. Der Ab-
stand zwischen dem Objekt und der Linse (also die Gegenstandsweite g) sollte ca. 60mm entsprechen. Wenn du nun mit
der Taschenlampe das Objekt beleuchtest, wirst du es in einem Abstand von ca. 300mm auf der Wand scharf sehen. Ein
Kinoprojektor hat statt des Objekts einen Filmstreifen und natürlich eine viel stärkere Lichtquelle.

Wie ist das Bild orientiert?

Schiebe die Linse in dem Würfel hin und her und be-
obachte, wann das Bild scharf ist. Finde das Bild für g =
60mm, 65mm, 70mm und messe den Abstand zwischen

Benutze eine Taschenlampe (z.B. von deinem Handy)
als Lichtquelle und halte es vor das Objekt.

der Linse und dem Bild.

# So funktioniert der Projektor

Wo ist das Bild?
Bei der Abbildung eines Gegenstands durch eine Sammellinse hängen Lage und Größe des Bildes von der Entfernung (g) des Gegenstands zur Linse und von deren Brennweite (f) ab.
Die Linsengleichung beschreibt den Zusammenhang zwischen der Bildweite (b) und Objektweite (g):

Wie groß ist das Bild?
Die Vergrößerung des Objekts auf dem Schirm lässt sich einfach mit der folgenden Formel ausrechnen:
2xf | f | 2xf

Brennweite
f
Entfernung des Gegen- | Entfernung des Bildes

Bildgröße B

Gegenstandsgrö-

g | b
1
ff = 1
gg

+

1
bb

# VV = bb

# gg = BB

GG

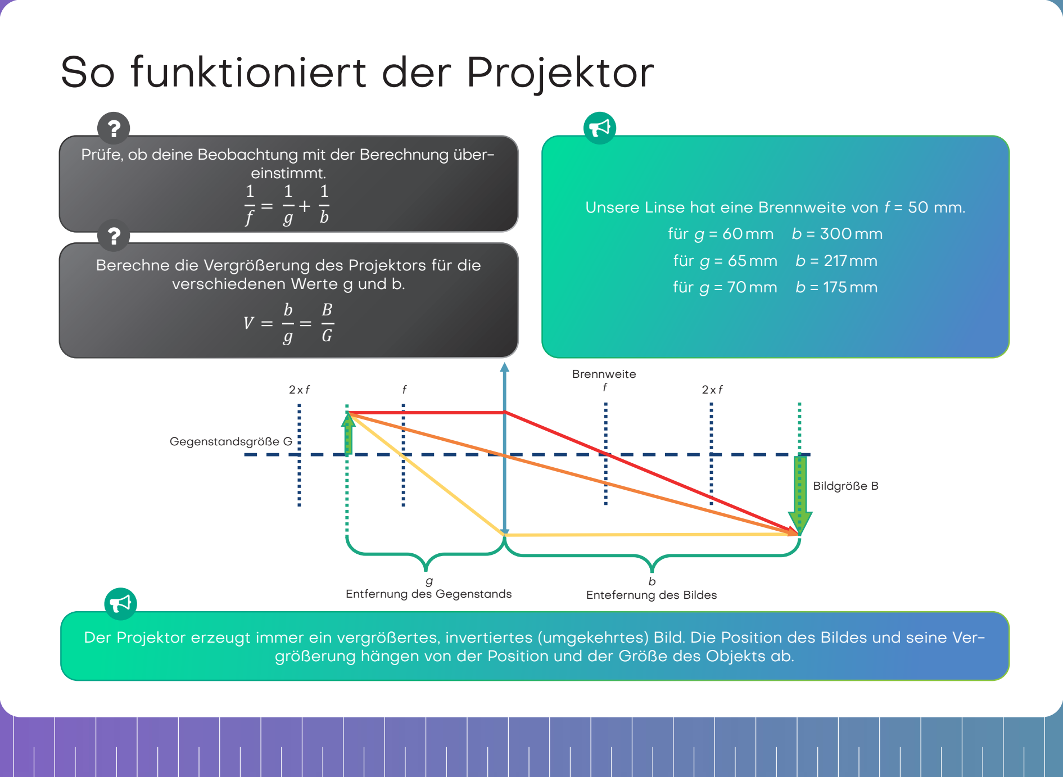
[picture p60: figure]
einstimmt.; verschiedenen Werte g und b.; Brennweite f; Gegenstandsgröße G; g Entfernung des Gegenstands; b Entefernung des Bildes; So funktioniert der Projektor; für g = 60mm b = 300mm für g = 65mm b = 217mm für g = 70mm b = 175mm; Bildgröße B

Prüfe, ob deine Beobachtung mit der Berechnung über-

Berechne die Vergrößerung des Projektors für die

Unsere Linse hat eine Brennweite von f = 50 mm.

Der Projektor erzeugt immer ein vergrößertes, invertiertes (umgekehrtes) Bild. Die Position des Bildes und seine Vergrößerung hängen von der Position und der Größe des Objekts ab.

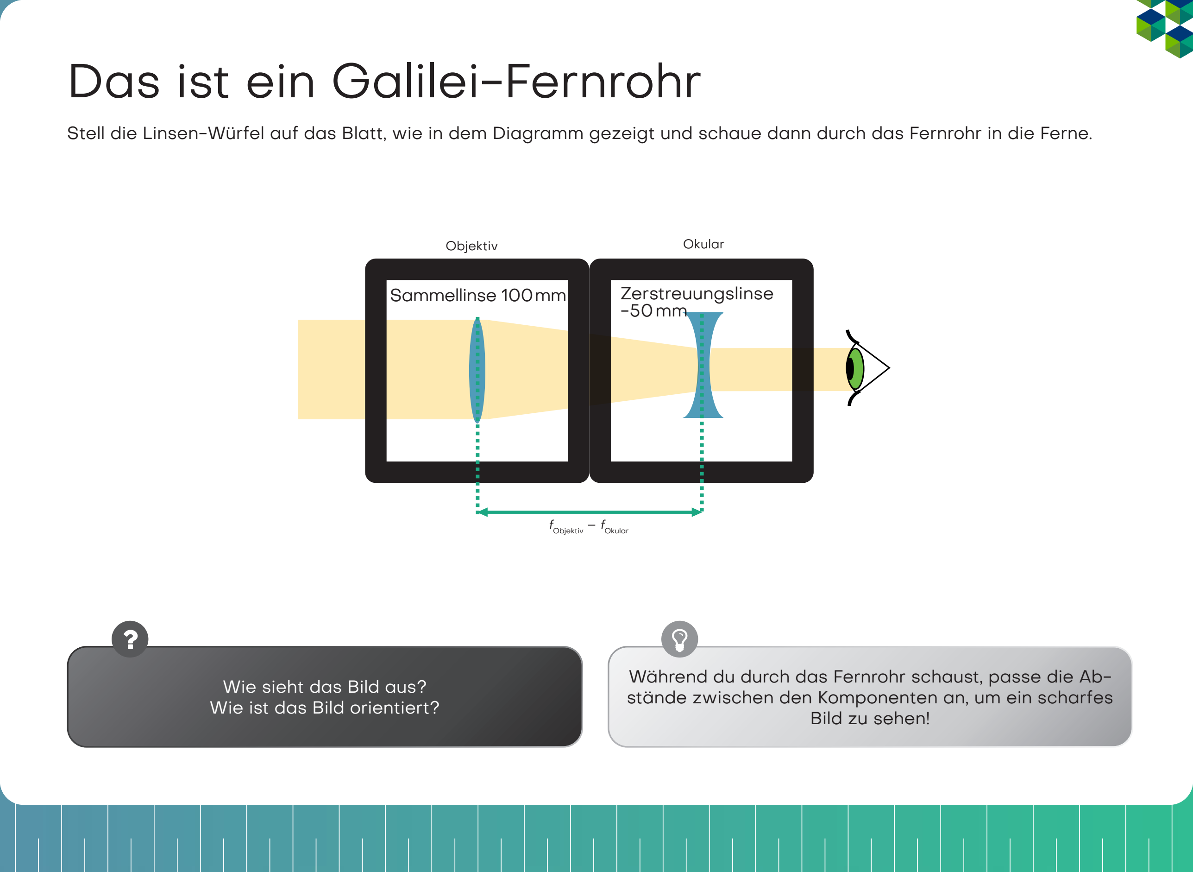
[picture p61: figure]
Das ist ein Galilei-Fernrohr; fObjektiv – fOkular; Wie sieht das Bild aus? Wie ist das Bild orientiert?; Bild zu sehen!; Zerstreuungslinse -50mm; Okular; Sammellinse 100mm; Objektiv

Stell die Linsen-Würfel auf das Blatt, wie in dem Diagramm gezeigt und schaue dann durch das Fernrohr in die Ferne.

Während du durch das Fernrohr schaust, passe die Abstände zwischen den Komponenten an, um ein scharfes

# So funktioniert das Galilei-Fernrohr

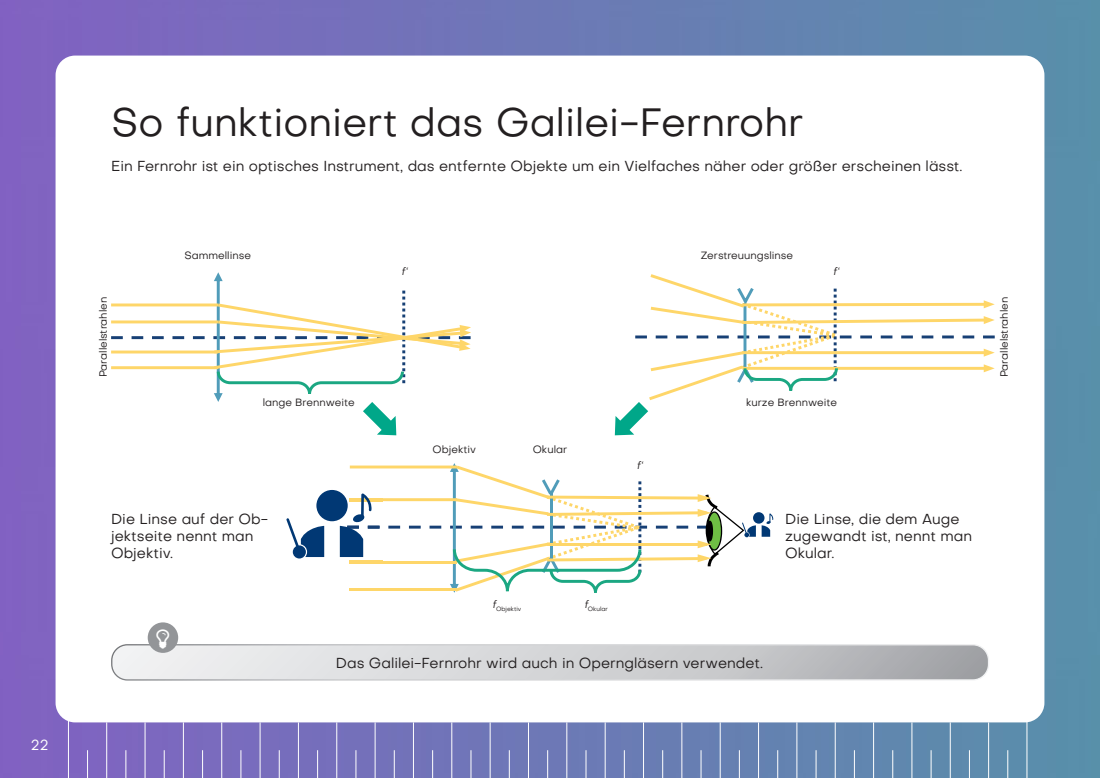
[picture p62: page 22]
Sammellinse; Zerstreuungslinse; lange Brennweite; kurze Brennweite; Parallelstrahlen; Objektiv; Okular; fObjektiv; fOkular

Ein Fernrohr ist ein optisches Instrument, das entfernte Objekte um ein Vielfaches näher oder größer erscheinen lässt.

Die Linse auf der Ob-
jektseite nennt man
Objektiv.

Die Linse, die dem Auge
zugewandt ist, nennt man
Okular.

Das Galilei-Fernrohr wird auch in Operngläsern verwendet.

# So funktioniert das Galilei-Fernrohr

Wie lautet die Vergrößerung dieses Galilei-Fernrohrs?

Formel zur Berechnung der Vergrößerung

Sichtfeld bezeichnet den Bereich im Bildwinkel einer optischen Einrichtung, innerhalb dessen Objekte aufgezeichnet wer-
den können.

Das Bild ist immer
• vergrößert mit der Vergrößerung aus obiger Formel
• aufrecht
• seitenrichtig
Das Sichtfeld ist klein.

Mit diesem Fernrohr kann man keine sehr hohe Vergrö-
ßerung erreichen. Dafür ist es sehr kompakt.

# Das ist ein Kepler-Fernrohr

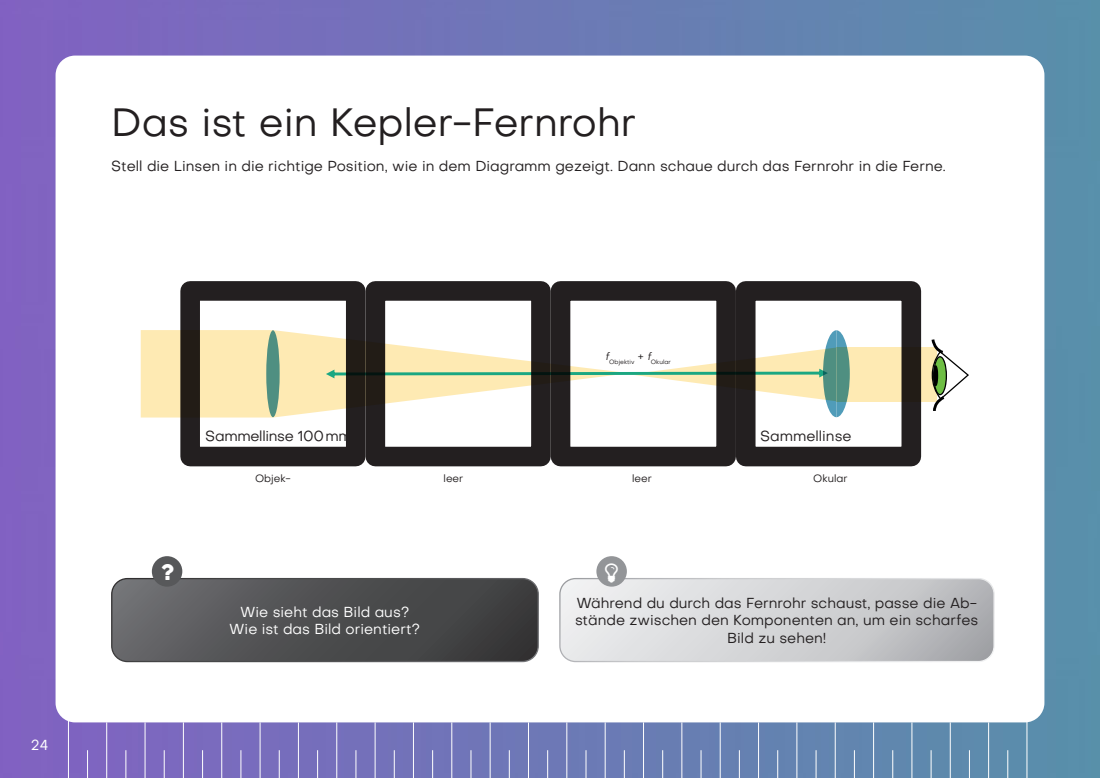
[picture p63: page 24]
fObjektiv + fOkular; Objek-; Okular; Sammellinse; leer; Sammellinse 100mm

Stell die Linsen in die richtige Position, wie in dem Diagramm gezeigt. Dann schaue durch das Fernrohr in die Ferne.

Während du durch das Fernrohr schaust, passe die Ab-
stände zwischen den Komponenten an, um ein scharfes

Wie sieht das Bild aus?
Wie ist das Bild orientiert?

Bild zu sehen!

# So funktioniert das Kepler-Fernrohr

Diese Art von Fernrohr wird häufig in der Astronomie benutzt.

# So funktioniert das Kepler-Fernrohr

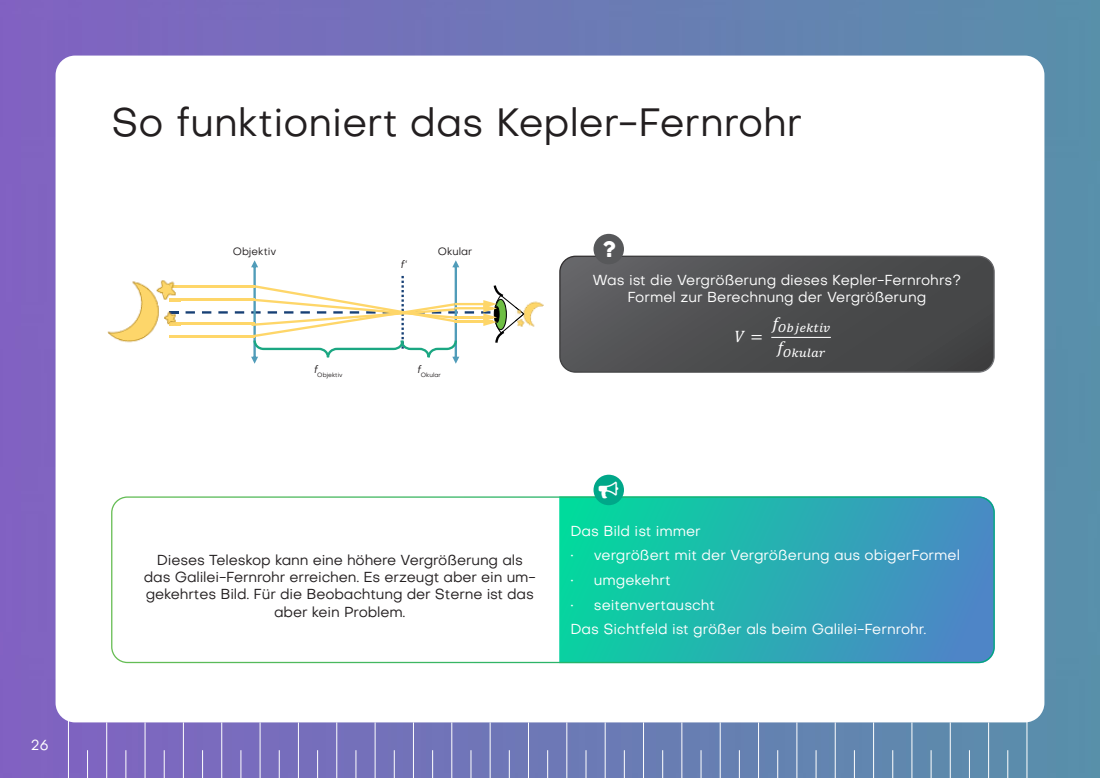
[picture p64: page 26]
Objektiv; Okular; fObjektiv; fOkular

Was ist die Vergrößerung dieses Kepler-Fernrohrs?

Formel zur Berechnung der Vergrößerung

Das Bild ist immer
• vergrößert mit der Vergrößerung aus obigerFormel
• umgekehrt
• seitenvertauscht
Das Sichtfeld ist größer als beim Galilei-Fernrohr.

Dieses Teleskop kann eine höhere Vergrößerung als
das Galilei-Fernrohr erreichen. Es erzeugt aber ein um-
gekehrtes Bild. Für die Beobachtung der Sterne ist das

aber kein Problem.

# Das ist ein Beobachtungsfernrohr

Das Beobachtungsfernrohr ist lang, deshalb ist das Schema hier nicht so groß wie in der Realität. Stell‘ die Linsen in die
richtige Position wie hier dargestellt und schaue durch das Fernrohr in die Ferne.

Während du durch das Fernrohr schaust, passe die Ab-
stände zwischen den Komponenten an, um ein scharfes

Wie sieht das Bild hier im Vergleich zum Kepler-Fernrohr

Bild zu sehen!

# So funktioniert das Beobachtungsfernrohr

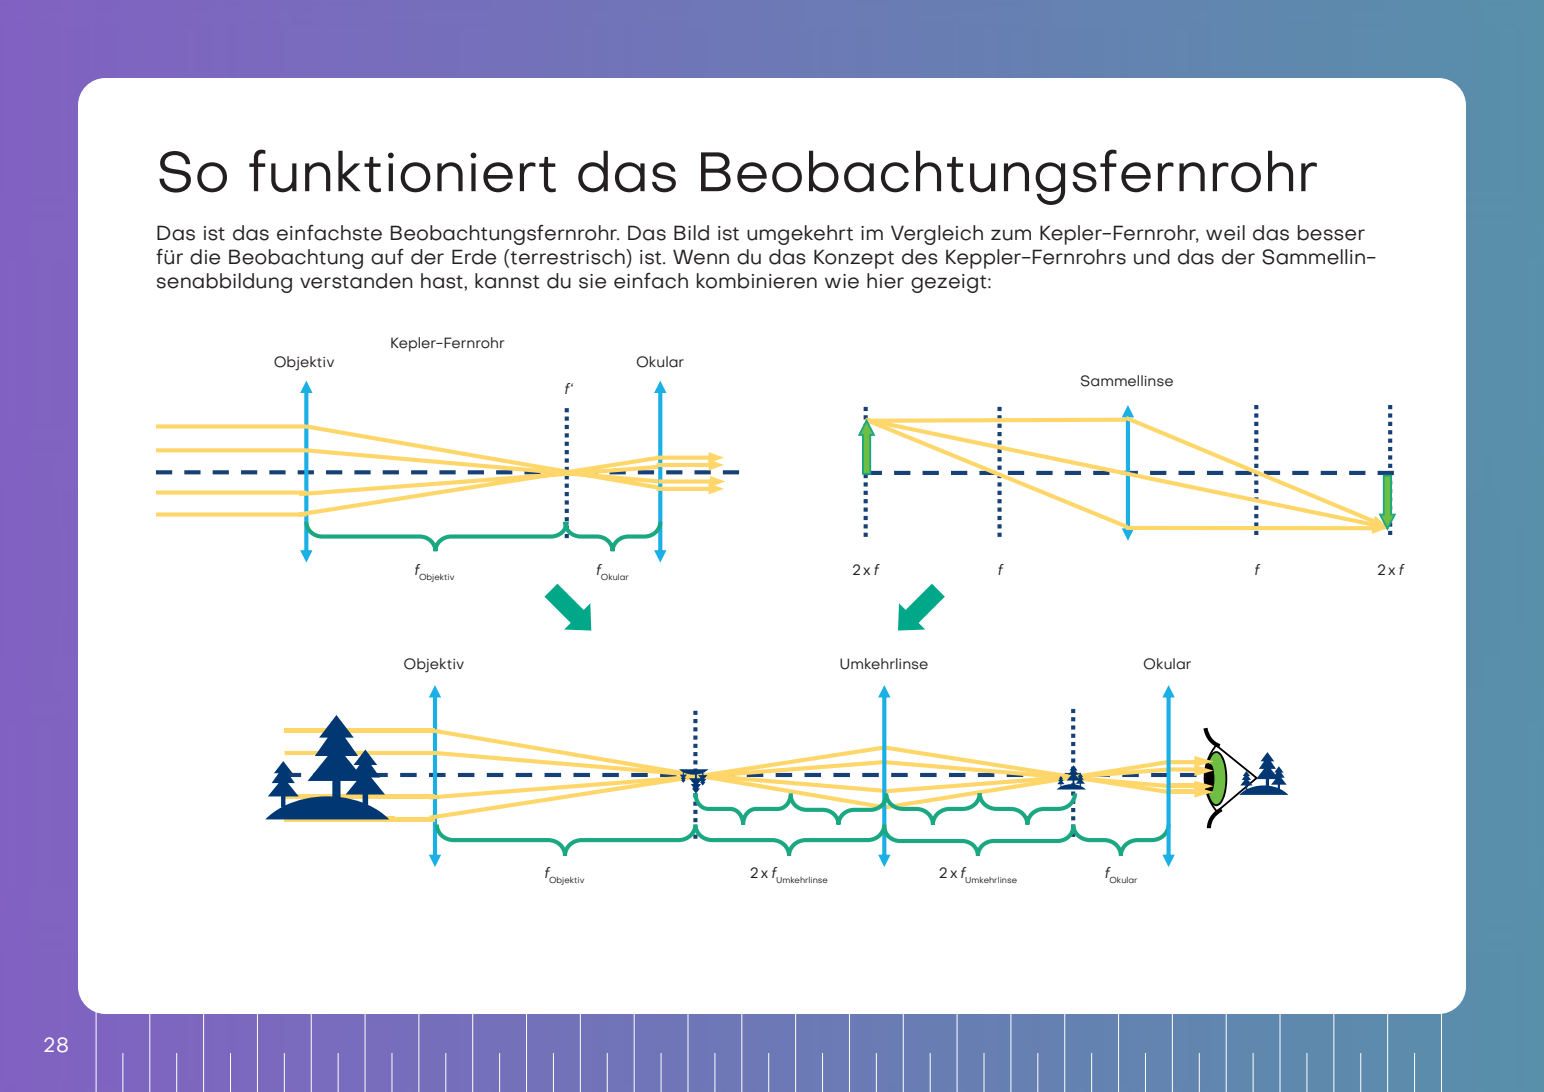
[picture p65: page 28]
Kepler-Fernrohr; Okular; fOkular; 2xfUmkehrlinse; Sammellinse; Objektiv; Umkehrlinse; fObjektiv

Das ist das einfachste Beobachtungsfernrohr. Das Bild ist umgekehrt im Vergleich zum Kepler-Fernrohr, weil das besser
für die Beobachtung auf der Erde (terrestrisch) ist. Wenn du das Konzept des Keppler-Fernrohrs und das der Sammellin-
senabbildung verstanden hast, kannst du sie einfach kombinieren wie hier gezeigt:

# So funktioniert das Beobachtungsfernrohr

Die Vergrö-
ßerung ist so
wie die des
Kepler-Fern-
rohrs. Die Um-
kehrlinse ver-
ändert nur die
Orientierung
(das Bild wird
umgekehrt),
nicht die Ver-
größerung.
Vergrößerung

Das Bild ist
• vergrößert mit der gleichen Vergrößerung wie mit
dem Keppler Fernrohr
• aufrecht
• seitenrichtig

Für terrestrische Beobachtungen ist ein aufrechtes
Bild notwendig. Echte terrestrische Teleskope ver-
wenden Prismensysteme, um das Bild zu drehen und

kompakt zu halten.

# Lichtmikroskop mit „Unendlich-Optik“

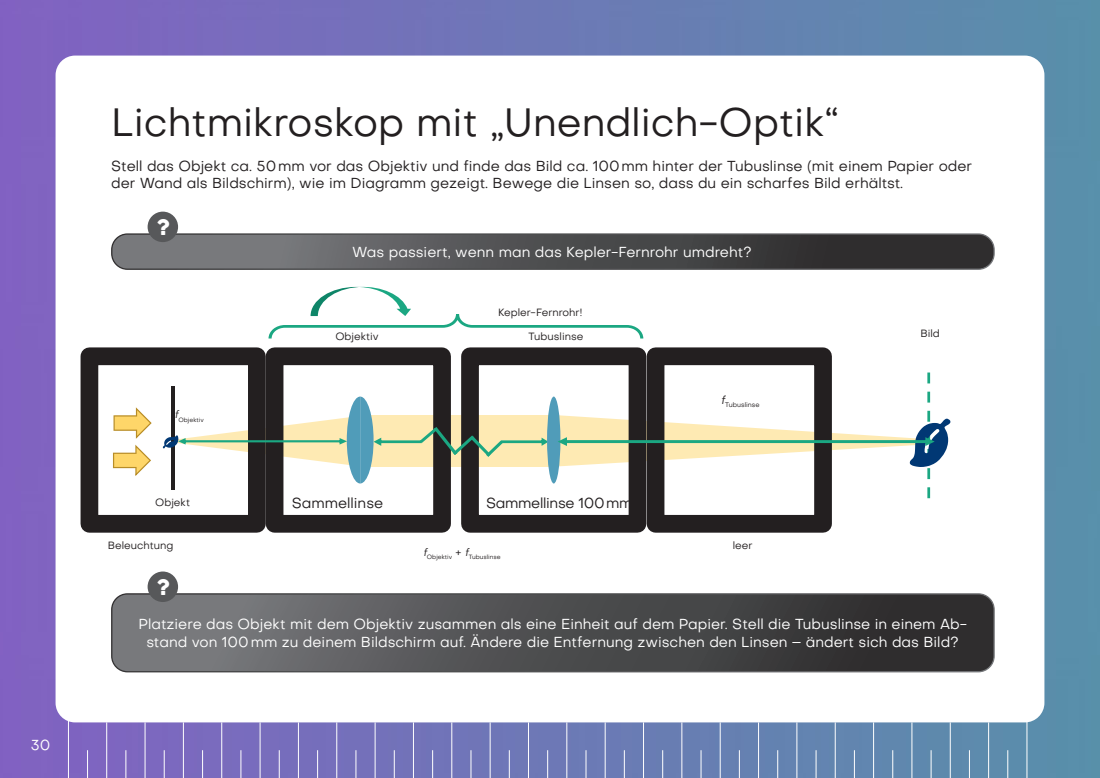
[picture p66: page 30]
leer; Sammellinse; Sammellinse 100mm; Objektiv; Beleuchtung; fObjektiv + fTubuslinse; Tubuslinse; Bild; Kepler-Fernrohr!; Objekt; fObjektiv; fTubuslinse

Stell das Objekt ca. 50mm vor das Objektiv und finde das Bild ca. 100mm hinter der Tubuslinse (mit einem Papier oder
der Wand als Bildschirm), wie im Diagramm gezeigt. Bewege die Linsen so, dass du ein scharfes Bild erhältst.

Was passiert, wenn man das Kepler-Fernrohr umdreht?

Platziere das Objekt mit dem Objektiv zusammen als eine Einheit auf dem Papier. Stell die Tubuslinse in einem Ab-
stand von 100mm zu deinem Bildschirm auf. Ändere die Entfernung zwischen den Linsen – ändert sich das Bild?

# Das bedeutet „Unendlich-Optik“

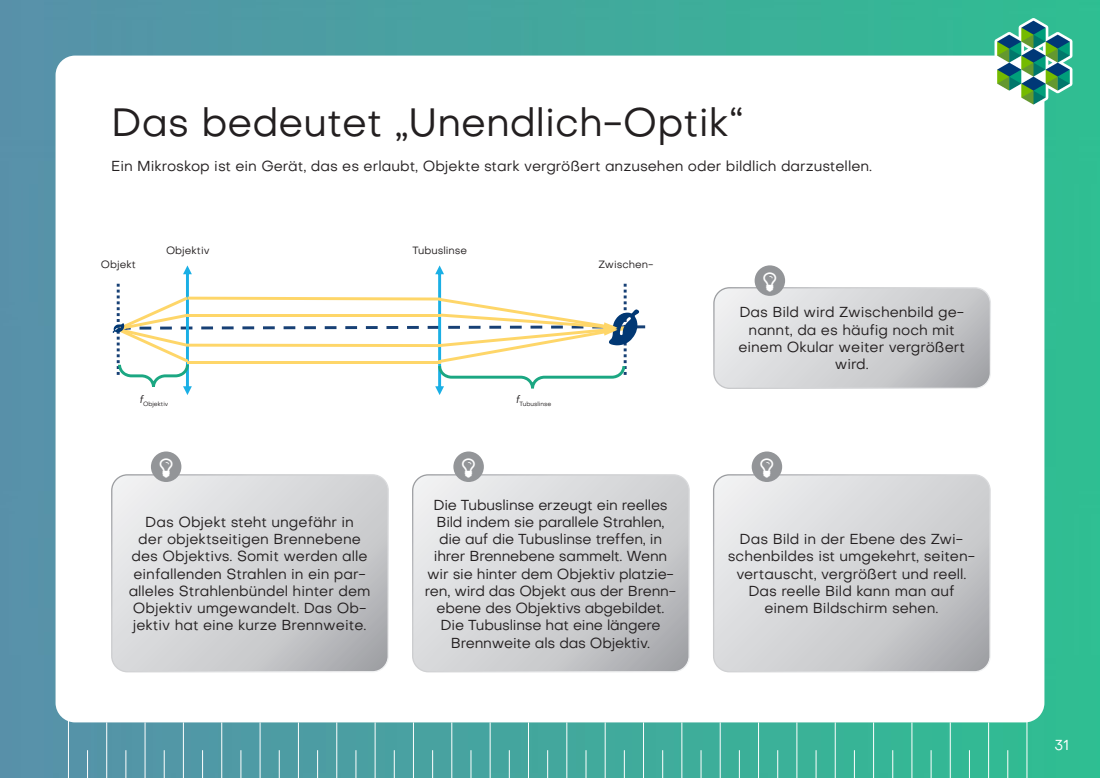
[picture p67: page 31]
wird.; Objektiv; Tubuslinse; Objekt; Zwischen-; fObjektiv; fTubuslinse

Ein Mikroskop ist ein Gerät, das es erlaubt, Objekte stark vergrößert anzusehen oder bildlich darzustellen.

Das Bild wird Zwischenbild ge-
nannt, da es häufig noch mit
einem Okular weiter vergrößert

Die Tubuslinse erzeugt ein reelles
Bild indem sie parallele Strahlen,
die auf die Tubuslinse treffen, in
ihrer Brennebene sammelt. Wenn
wir sie hinter dem Objektiv platzie-
ren, wird das Objekt aus der Brenn-
ebene des Objektivs abgebildet.
Die Tubuslinse hat eine längere
Brennweite als das Objektiv.

Das Objekt steht ungefähr in
der objektseitigen Brennebene
des Objektivs. Somit werden alle
einfallenden Strahlen in ein par-
alleles Strahlenbündel hinter dem
Objektiv umgewandelt. Das Ob-
jektiv hat eine kurze Brennweite.

Das Bild in der Ebene des Zwi-
schenbildes ist umgekehrt, seiten-
vertauscht, vergrößert und reell.
Das reelle Bild kann man auf
einem Bildschirm sehen.

# Das bedeutet „Unendlich-Optik“

Ein Mikroskop ist ein Gerät, das es erlaubt, Objekte stark vergrößert anzusehen oder bildlich darzustellen.

Was ist die Vergrößerung des Bildes?

Die Linsen des Kepler-Fernrohrs können auch für ein Mikroskop verwendet werden, aber in einer anderen Reihenfolge.
Solange das Objekt in der Brennebene des Objektivs und der Bildschirm in der Brennebene der Tubuslinse ist, ist die

Entfernung zwischen Objektiv und Tubuslinse egal, weil die Lichtstrahlen parallel sind.

# „Unendlich-Optik“-Mikroskop mit Okular

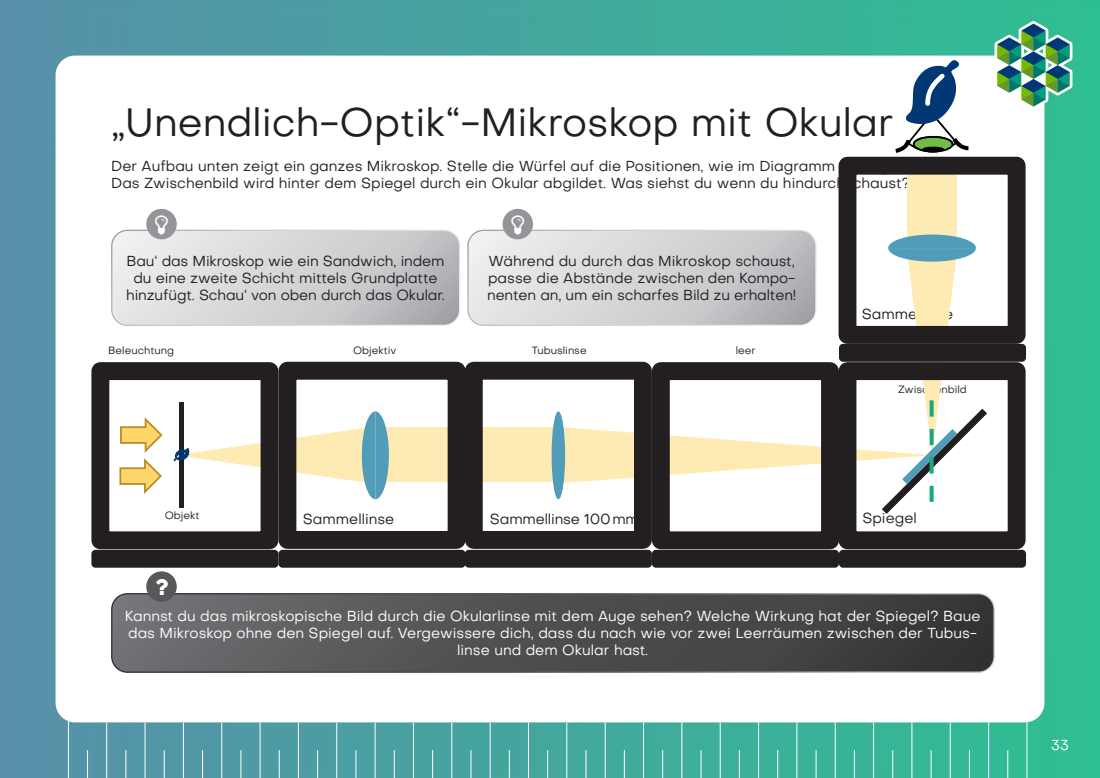
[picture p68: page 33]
Beleuchtung; Objektiv; Tubuslinse; Objekt; Okular; Zwischenbild; leer; Sammellinse; Sammellinse 100mm; Spiegel

Der Aufbau unten zeigt ein ganzes Mikroskop. Stelle die Würfel auf die Positionen, wie im Diagramm gezeigt.
Das Zwischenbild wird hinter dem Spiegel durch ein Okular abgildet. Was siehst du wenn du hindurchschaust?

Bau‘ das Mikroskop wie ein Sandwich, indem
du eine zweite Schicht mittels Grundplatte
hinzufügt. Schau‘ von oben durch das Okular.

Während du durch das Mikroskop schaust,
passe die Abstände zwischen den Kompo-
nenten an, um ein scharfes Bild zu erhalten!

Kannst du das mikroskopische Bild durch die Okularlinse mit dem Auge sehen? Welche Wirkung hat der Spiegel? Baue
das Mikroskop ohne den Spiegel auf. Vergewissere dich, dass du nach wie vor zwei Leerräumen zwischen der Tubus-

linse und dem Okular hast.

# Dazu ist das Okular gut

Neuere Mikroskope sind mit einer sogenannten „Unendlich-Optik“ ausgestattet. In diesem Fall erzeugt das Objektiv kein
reelles Zwischenbild. Das Licht verlässt das Objektiv als unendliche parallele Strahlen. Am Ende von dem „unendlichen“
Tubus befindet sich
eine Tubuslinse. Diese erzeugt ein Zwischenbild, das dann wieder durch das Okular vergrößert wird.

Ein Filter kann dazu verwendet werden, die Helligkeit

„unendliche“ Tubuslänge, die beliebig groß oder klein sein kann

und Farbe des Bildes zu verändern.

Das Bild hinter dem Okular ist umgekehrt, seitenvertauscht, vergrößert und virtuell. Das virtuelle Bild kann man mit dem

Diese Konfiguration ist in modernen Mikroskopen sehr nützlich, da zusätzliche Komponenten wie Filter zwischen Objektiv

und Tubuslinse platziert werden können, ohne den optischen Pfad zu beeinträchtigen.

# Dazu ist das Okular gut

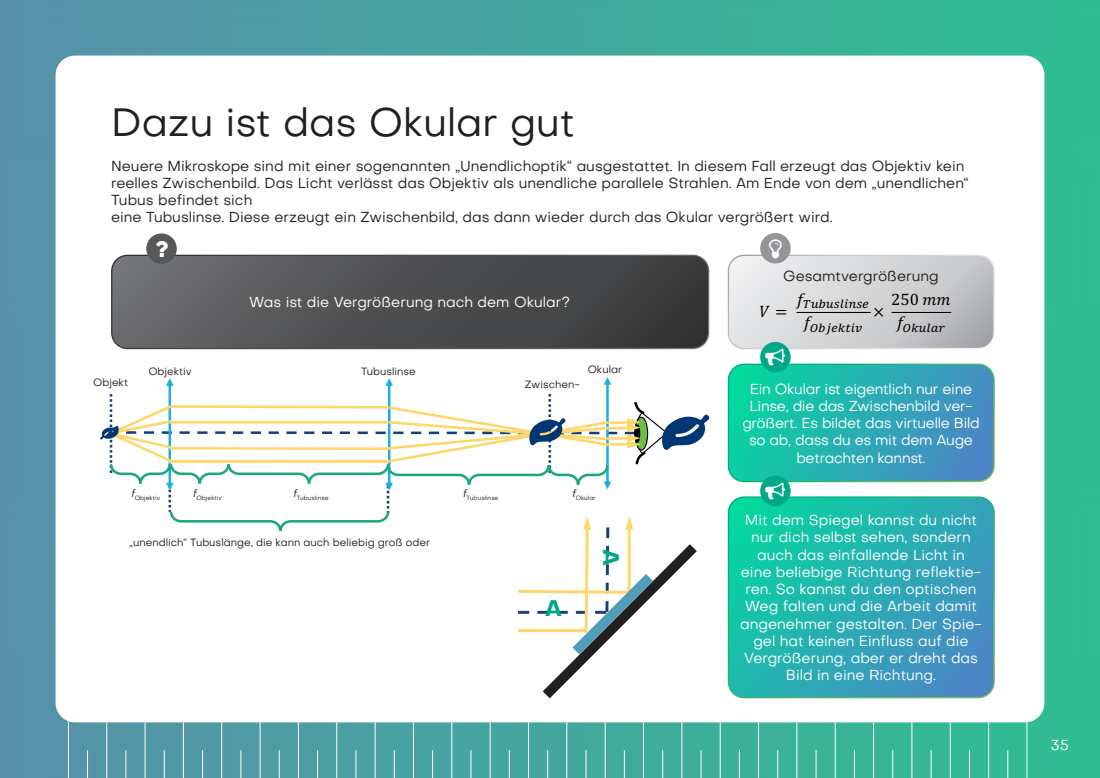
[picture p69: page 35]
Gesamtvergrößerung; Objektiv; Tubuslinse; Objekt; fObjektiv; fTubuslinse; fOkular; Okular; Zwischen-; 250 mmmm ff)+"%./

Neuere Mikroskope sind mit einer sogenannten „Unendlichoptik“ ausgestattet. In diesem Fall erzeugt das Objektiv kein
reelles Zwischenbild. Das Licht verlässt das Objektiv als unendliche parallele Strahlen. Am Ende von dem „unendlichen“
Tubus befindet sich
eine Tubuslinse. Diese erzeugt ein Zwischenbild, das dann wieder durch das Okular vergrößert wird.

Was ist die Vergrößerung nach dem Okular?

Ein Okular ist eigentlich nur eine
Linse, die das Zwischenbild ver-
größert. Es bildet das virtuelle Bild
so ab, dass du es mit dem Auge
betrachten kannst.
Mit dem Spiegel kannst du nicht
nur dich selbst sehen, sondern
auch das einfallende Licht in
eine beliebige Richtung reflektie-
ren. So kannst du den optischen
Weg falten und die Arbeit damit
angenehmer gestalten. Der Spie-
gel hat keinen Einfluss auf die
Vergrößerung, aber er dreht das
Bild in eine Richtung.

„unendlich“ Tubuslänge, die kann auch beliebig groß oder

# Lichtmikroskop mit „Endlich-Optik“

Stell‘ die Würfel auf die Positionen, wie unten im Diagramm gezeigt und schaue durch das
Okular.
Bau‘ das Mikroskop wie ein Sandwich indem du eine zweite Schicht
mittels Grundplatte hinzufügt. Schau‘ von oben durch das Okular.
Das Objektiv kann in der Linearstage hin und her bewegt werden.

Siehst du das Bild wie bisher durch das Okular? Kannst
du das echte Zwischenbild auch mit einem Blatt Papier

Drehe das kleine Zahnrad des Objektivhalters. Damit
bewegst bzw. fokussierst du das Objektiv. Wenn es nicht
weiter geht, kannst du auch das Objektiv in dem Halter

# „Endlich-Optik“ versus „Unendlich-Optik“

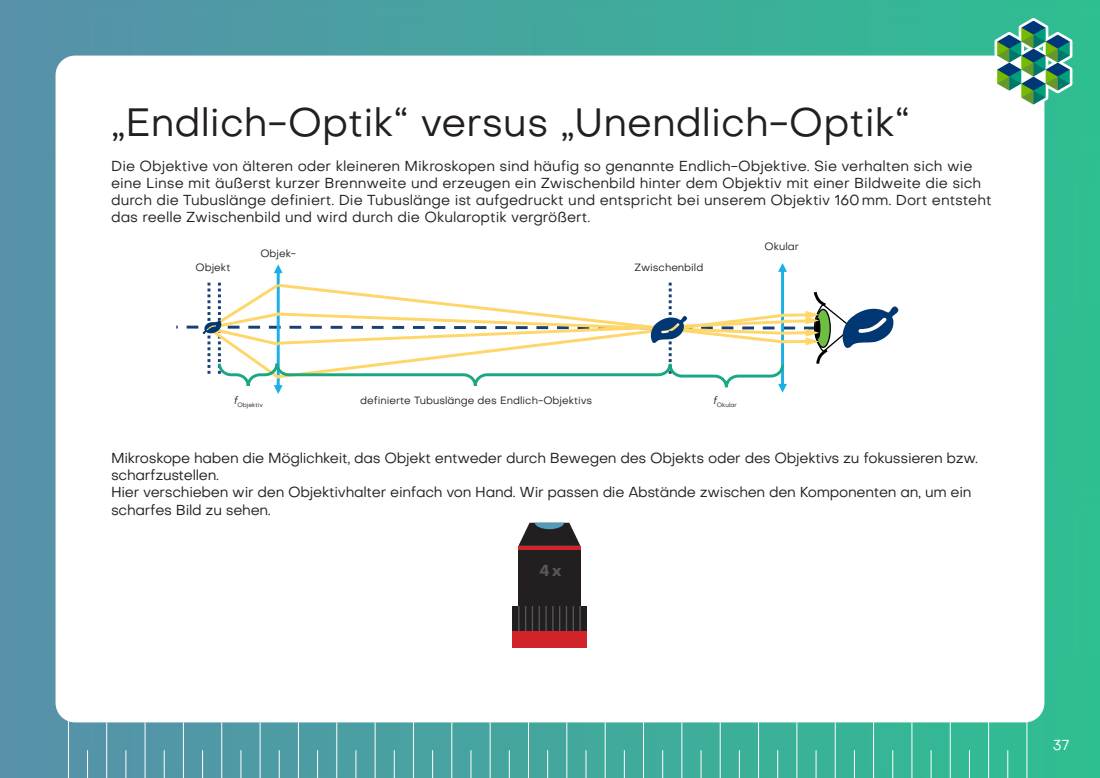
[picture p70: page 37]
Objekt; Objek-; Zwischenbild; Okular; fObjektiv; fOkular definierte Tubuslänge des Endlich-Objektivs

Die Objektive von älteren oder kleineren Mikroskopen sind häufig so genannte Endlich-Objektive. Sie verhalten sich wie
eine Linse mit äußerst kurzer Brennweite und erzeugen ein Zwischenbild hinter dem Objektiv mit einer Bildweite die sich
durch die Tubuslänge definiert. Die Tubuslänge ist aufgedruckt und entspricht bei unserem Objektiv 160mm. Dort entsteht
das reelle Zwischenbild und wird durch die Okularoptik vergrößert.

Mikroskope haben die Möglichkeit, das Objekt entweder durch Bewegen des Objekts oder des Objektivs zu fokussieren bzw.
scharfzustellen.
Hier verschieben wir den Objektivhalter einfach von Hand. Wir passen die Abstände zwischen den Komponenten an, um ein
scharfes Bild zu sehen.

# „Endlich-Optik“ versus „Unendlich-Optik“

Was ist die Vergrößerung des Zwischenbildes? Und was ist die Vergrößerung nach dem Okular?

wie darauf geschrieben

Das Bild ist größer als mit dem
Unendlich-Mikroskop. Die Vergrö-
ßerung des Objektivs beträgt hier
4x. Wenn du die Vergrößerung mit
dem vorherigen Mikroskop be-
rechnet hast, überrascht dich das

Das Zwischenbild wird jetzt nur
noch durch das Objektiv gebildet
und liegt 160 mm dahinter. Wir
werden im nächsten Schritt her-
ausfinden, warum.

definierte Tubuslänge des Endlich-Objek-

2 x Sammellinse 50mm

Schau‘ durch die einzelne 50-mm-Linse und dann durch die Doppellinse auf das Gitter.

Schau‘ durch die 50-mm-Linse und dann durch das Objektiv auf den kleinen Text.

Welche von den Linsen vergrößert stärker? Was steht
dort geschrieben? | Wie ändert sich die Vergrößerung und das Sichtfeld?

# Objektiv und Okular

Öffne die Würfel mit den 50-mm-Linsen. Platziere nun beide 50-mm-Linsen in einem Würfel, sodass die „Bäuche“ der Linsen aufeinander zeigen.

Schau‘ auf das Objektiv! Was ist da drin? Was steht darauf geschrieben?

Das Objektiv ist auch eine Sammellinse mit kurze Brennweite.

4/0.10
160/0.17

# Das ist das Objektiv

Ein Objektiv ist ein optisches System, das eine vergrößerte Abbildung eines Gegenstands erzeugt. Die verschiedenen auf dem Objektiv abgedruckten Zahlen haben verschiedene Bedeutungen:

Deckglaskorrektur :
Manchmal wird ein Deckglas verwendet, um die Probe zu versiegeln. Ein Objektiv muss für diese Dicke (0,17mm) korrigiert werden.

Numerische Apertur:
Sie bestimmt die Fähigkeit, Licht aufzusammeln und somit die optische Auflösung.

Tubuslänge:
∞ steht für unendlich, 160 steht für 160 mm und ist die am häufigsten verwendete Tubuslänge nach DIN

Vergrößerung:
Gängige Vergrößerungen
sind 4x, 10x, 40x, 100x.

Das 4x Objektiv hat nur eine Linse drin. Die Objektive mit stärkerer Vergrößerung sind ganze Linsensysteme.

Das Objektiv ist auch eine Sammellinse mit kurzer Brennweite. Das 4x Objektiv hat eine Brennweite von f=32mm. Wenn es als Lupe verwendet wird, hat es eine höhere Vergrößerung als die 50-mm Linse. Das Sichtfeld ist scharf, aber klein.

4/0.10
160/0.17

# Das ist das Okular

d = 2/3 fLinse; Zwischenbild; VV = 250 mmmm 3 4 ff!"#$%

Ein Okular ist eigentlich eine Lupe, da es das Zwischenbild vergrößert. Das Okular, was wir hier verwenden, ist ein sogenanntes
Ramsden-Okular.
Eine einzelne Linse kann auch als Okular benutzt werden. Allerdings ist bei dem, aus einem Linsensystem bestehenden,
Ramsden-Okular das Sichtfeld besser, weil es weniger Fehler am Rand des Sichtfelds erzeugt. Das Ramsden-Okular be-
steht aus zwei Linsen mit der gleichen Brennweite. Seine Brennweite beträgt fRamsden-Okular= 3/4 fLinse

Was ist die Vegrößerung des Ramsden-Okulars?

Der Abbildungsmaßstab ist bei kurzen Objektabständen
höher als bei einem einzelnen 50-mm-Objektiv.

Jedes Okular hat eine so genannte Ramsden-Scheibe,
das ist der kleinste Durchmesser des Lichtstrahls, der
aus dem Mikroskop durch das Okular austritt.

Das Sichtfeld ist größer und das Bild sieht mit dem

Ramsden-Okular klarer aus.

# Smartphone Mikroskop

Baue das Smartphone Mikroskop wie dargestellt. Nutze zwei beliebi-
ge Würfel, um das Smartphone sicher zu platzieren.

Bau‘ das Mikro-
skop wie ein
Sandwich, in-
dem du eine
zweite Schicht
mittels Grund-
platte hinzufügt.
Schau von oben
durch das Oku-

Tausche das
Ramsden-Oku-
lar mit der
50-mm-Linse
aus. Was eignet
sich besser für
das Auge und
was für das
Smartphone?

# Besser mit Smartphone oder Auge?

dation.; jekte in; Akkommodation; Autofokus

Die Smartphone Kamera hat eine Linse mit sehr kurzer Brennweite, da diese in das dünne Smartphone passen muss. Die Linse
erzeugt dann ein Bild auf dem Kamera-Sensor, dessen Eingeschaften dem menschlischen Auge ähneln.
Das Auge kann die Objekte sowohl aus der Ferne als auch aus der Nähe abbilden. Diese Eigenschaft heißt Akkommo-
Die Smartphone-Kamera kann das auch, es wird allerdings als Autofokus bezeichnet. Es beschreibt die Fähigkeit, Ob-

Das Bild aus dem Okular kommt in parallelen Strahlen, als käme es aus dem Unendlichen. Es wurde mit einem ent-

spannten Auge (Blick in die Ferne) oder mit einer auf Unendlich fokussierten Kamera beobachtet.

# Besser mit Smartphone oder Auge?


Um das Bild des Mikroskops sehen zu können, muss die Pupille – also die „Blende“, die den Einfall des Lichts begrenzt, mit der
Ramsden-Scheibe des Okulars übereinstimmen. Die Pupille des Auges ist in dessen Inneren fixiert und kann nicht näher an das
Okular herangeholt werden. Die Pupille der Smartphone-Kamera ist hingegen sehr nahe an der Oberfläche des Handys. Wegen
dieses Unterschieds braucht man eine unterschiedliche Entfernung zum Okular für das Auge und die Kamera.

Was is die Vergrößerung dieses Mikroskops?
Formel zur Berechnung der Vergrößerung

Beim Ramsden-Okular ist die Ramsden-Scheibe näher
am Würfel und hat einen kleineren Durchmesser, was für

die Smartphone-Kamera gut funktioniert.

Pupille des Auges

Die Ramsden-Scheibe der einzelnen 50mm-Linse hat
einen größeren Durchmesser und ist daher für die Beob-
achtung der Probe mit dem Auge bequemer. Durch das
Okular sieht es so aus, als ob das Bild auf dem Spiegel
darunter liegt. Die 50 mm-Objektive haben einen gro-
ßen Durchmesser, so dass bei der Verwendung eines
einzigen Objektivs als Okular das Sichtfeld durch die
Größe der Spiegel eingeschränkt wird.

Pupille der Kamera

Berechnungsergebnisse; Lupe; Projektor; Galilei-Fernrohr; Kepler-Fernrohr; „Unendlich“-Mikroskop; „Unendlich“-Mikroskop mit Okular; „Endlich“-Mikroskop - Zwischenbild; Ramsden-Okular; Smartphone Mikroskop mit Ramsden-Okular

## „Endlich“-Mikroskop - Gesamtvergrößerung

# Glossar

Lichtstrahl
Ein Pfeil oder eine Linie, die die Richtung des Lichts anzeigt; Wenn nicht anders gesagt, kommt das Licht in den Schemata immer von der linken Seite.
Linse
Ein transparenter lichtbrechender Körper z.B. aus Glas oder Plastik
Dünne Linse
Ein Modell einer Linse, das davon ausgeht, dass sie kein Volumen hat
Sammellinse
Eine Linse, die das einfallende Licht konvergiert (sammelt) Zerstreuungslinse
Eine Linse, die das einfallende Licht auffächert Brennpunkt F (Objektbrennpunkt), F‘ (Bildbrennpunkt) Ein Punkt, an dem das Licht gebündelt wird (Sammellinse) oder von dem es auseinander zu laufen scheint (Zerstreuungslinse)
Brennweite f
Der Abstand zwischen dem Brennpunkt & der dünnen Linse Brennebene
Eine Ebene parallel zur dünnen Linse, die durch den Brennpunkt verläuft

Optische Achse
Das Grundgerüst für jede optische Skizze; sie verläuft durch die Mitte der Linse und steht senkrecht zur Linsenebene Virtuelles Bild
Ein durch eine Linse oder ein optisches System erzeugtes Bild, das von einem menschlichen Auge durch das System betrachtet werden kann
Reelles Bild
Ein durch eine Linse oder ein optisches System erzeugtes Bild, das auf einem Bildschirm hinter dem System betrachtet werden kann
Vergrößerung
Ein Verhältnis der Bildgröße und der Objektgröße (für ein reales Bild); ein Verhältnis des beobachteten Bildes und der Objektgröße (für ein virtuelles Bild)
Gegenstand
Ein Objekt, das wir mit der Linse abbilden wollen; die Größe des Objekts ist G
Entfernung g des Gegestands
Der Abstand zwischen dem Objekt und der dünnen Linse Bild
Eine Abbildung des Gegenstands; Größe des Bildes ist B.

Objektseite
Seite in Bezug auf die Linse, auf den sich das Objekt (Gegenstand) befindet; links in den Schemata
Bildseite
Seite in Bezug auf die Linse, auf der das reelle Bild entsteht; Das virtuelle Bild befindet sich auf der gleichen Seite wie das Objekt.
Mittelpunktstrahl
Mittelpunktstrahlen durchlaufen die dünne Linse unverändert.
Parallelstrahlen
Alle Strahlen, die parallel zur optischen Achse laufen, werden durch die Linse so gebrochen, dass sie sich in dem Brennpunkt treffen. Als hellester Punkt direkt hinter der Linse findet sich dieser nur bei Sammellinsen. Brennpunktstrahlen
Alle Strahlen, die durch einen Brennpunkt verlaufen oder aus dem Brennpunkt kommen, werden durch die Linse so gebrochen, dass sie hinter der Linse parallel zur optischen Achse verlaufen.
Beleuchtung
In der Mikroskopie brauchst du eine Beleuchtungsquelle, um das Objekt sehen zu können. Das kann z.B. eine Taschenlampe oder die Reflektion von der Sonne sein.
Lupe (auch Vergrößerungsglas oder Brennglas)
Das einfachste optische Gerät, das das Objekt für das menschliche Auge vergrößert

Fernrohr (auch Linsenfernrohr oder Refraktor)
Ein optisches Instrument, bei dessen Nutzung entfernte Objekte um ein Vielfaches näher oder größer erscheinen Objektiv
Ein optisches System, das eine reelle optische Abbildung eines Gegenstandes erzeugt
Okular
Der augenseitige Teil eines optischen Systems Lichtmikroskop
Ein Mikroskop, das stark vergrößerte Bilder von kleinen Strukturen oder Objekten mit Hilfe von Licht erzeugt Tubuslinse
Eine Linse, die nach dem Unendlich-Optik-Objektiv aus den parallelen Lichtstrahlen ein reelles Zwischenbild erzeugt Zwischenbild
Vergrößerndes Bild des Objekts, das vom Objektiv erzeugt wird
Spiegel
Eine reflektierende Fläche, glatt genug, damit an ihr reflektiertes Licht ein Abbild erzeugen kann
Akkomodation des Auges
Eine dynamische Anpassung der Brechkraft des Auges; Sie führt dazu, dass Objekte verschiedener Entfernung scharf auf der Netzhaut abgebildet werden können.
Autofokus
Anders als bei der Akkomodation, bleibt in den meisten Fällen eines Autofokus die Brennweite konstant und der Ab-

# Impressum

Productdesign: Barbora Maršíková, Benedict Diederich

Layout: Katrin Uhlig, Benedict Diederich www.openUC2.com

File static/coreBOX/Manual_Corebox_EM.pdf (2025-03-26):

# CoreBOX

## UC2 Handbuch

openUC2
GmbHHans-Knöll-Str. 6
07745 Jena, Germany
E-Mail: hello@openuc2.com
Webseite: www.openuc2.com

Handbuch-Version: 0.1 – März 2025
Schnellanleitung zur ersten Nutzung

Lesen Sie zuerst sorgfältig die Sicherheitshinweise.
Stellen Sie sicher, dass die Montage auf einer ebenen, stabilen Oberfläche erfolgt. Besuchen Sie openuc2.github.io oder forum. openuc2.com, um detaillierte Montage- und Nutzungshinweise zu erhalten.
Rechtliche Informationen

Dieses Handbuch enthält wichtige Informationen zur sicheren und korrekten Nutzung Ihres openUC2-Produkts. Bitte beachten Sie, dass Nichtbeachtung der hierin enthaltenen Anweisungen zu Schäden am Produkt, persönlicher Verletzung oder eingeschränkter Leistung führen kann. Die openUC2 GmbH übernimmt keinerlei Haftung für Schäden, die durch Missbrauch, unsachgemäße Handhabung oder Nichtbeachtung der Handbuchinformationen verursacht werden.

Herstellerkontakt:
openUC2 GmbH
Hans-Knöll-Str. 6
07745 Jena
Germany
E-Mail: hello@openuc2.com
Web: www.openuc2.com

Ausführliche Online-Dokumentation:
Deutsch: https://openuc2.github.io/docs/Toolboxes/DiscoveryCore/GERMAN/uc2miniboxDE
Englisch: https://openuc2.github.io/docs/Toolboxes/DiscoveryCore/ENGLISH/uc2miniboxEN
Support
Bei Fragen, Problemen oder Unklarheiten überprüfen Sie zuerst die letzten Kapitel dieses Handbuchs oder besuchen Sie unsere Support-Website unter support.openuc2.com für eine vollständige Liste häufig gestellter Fragen, Fehlerbehebungen und detaillierte Anleitungen. Weitere Unterstützung erhalten Sie im Community-Forum unter forum.openuc2.com oder per E-Mail unter hello@ openuc2.com.
Sicherheitshinweise

Verwenden Sie das Gerät stets gemäß den Anweisungen in diesem Handbuch. Trennen Sie das Gerät unbedingt von der Stromversorgung, bevor Sie Wartungsarbeiten durchführen. Stellen Sie das Gerät stets auf einer stabilen Oberfläche auf, um Kippen oder Herunterfallen zu verhindern.
Optische Komponenten können empfindlich sein; gehen Sie sorgsam mit Spiegeln, Linsen und anderen zerbrechlichen Teilen um, um Verletzungen zu vermeiden.

Achten Sie auf Kleinteile und Magnete, die von Kindern verschluckt werden könnten. Halten Sie diese von Kindern fern.
Bei beschädigten Teilen kontaktieren Sie umgehend unseren Support unter support.openuc2.com.
Sorgen Sie für ausreichende Belüftung bei der Nutzung optischer Komponenten, insbesondere bei LED- oder Laser-basierten Modulen.


Entsorgung
Dieses Produkt darf nicht mit dem normalen Hausmüll entsorgt werden. Bitte bringen Sie das Gerät zur fachgerechten Entsorgung zu einer zugelassenen Sammelstelle für Elektroschrott oder wenden Sie sich für weitere Informationen zur korrekten Entsorgung an die örtlichen Behörden oder an die openUC2 GmbH.

Lizenz
Das UC2-System basiert auf dem offenen openUC2-Projekt (www.openuc2.com), das unter der CERN OHLv Lizenz veröffentlicht ist. Alle Dokumentationen, Baupläne und Software-Komponenten sind frei verfügbar unter github.com/openuc2. DieseAnleitung ist unter copyright von openUC2.

Kontaktdaten
openUC2 GmbH
Hans-Knöll-Str. 6
07745 Jena,
Deutschland
E-Mail: hello@openuc2.com
Webseite: www.openuc2.com

# What‘s inside?

Sample holder: holds the specimen.
Linear stage: changes the objective posi-
tion precisely.
Mirrors: reflect light.
Lenses: focus or defocus light.
Eyepiece: forms an image.
Objective: magnifies the sample image.
Eyepiece: Creates an image for the eye
Attention:

Please do not touch the glass!
Cleaning the lenses:
Use a lens cleaning cloth

Cube

Cube (Half)

Insert (e.g. Sample Holder)

Cube (Half)

Baseplate

# You.See.Too.? UC2!

The core element of the UC2 project is a simple cube. The cube consists of two halves and houses a sliding insert. The insert can hold different optical components (e.g. lenses, mirrors), which means that different functions can be realised with each cube. The cubes, as well as the base plates in puzzle format, which can be extended in all directions, are injection moulded and therefore have a high precision. The parts are held in place by a positive fit, which eliminates the need for magnets and screws. The inserts in stop plate format can be quickly adapted to new components and find space in the cube.

# Cube Type 1

Injection Molded with Formfit

The cube can be mounted on a base plate. The base plate modules can be put together like a jigsaw puzzle.

Baseplate

Baseplate with magnets

# UC2 for DIY 3D printing

In addition to the injection-mouldable design, the cube also comes in a printable version. Both cubes are compatible with each other, but the cube consisting of lid and body is easier to print. The magnetic screws are used to connect with the spherical magnets on the plate. By combining different cube modules, it is very easy to assemble different optical structures. A new function can be added with each cube. There are no limits to your creativity.

# Cube Type: 2

3D printed with magnetic connection

Baseplate

Cube

Cube (Body)

Screw (magnetic)

Ballmanget

Cube (Lid)

Small spherical magnets are embedded in the 3D-printed base plate, onto which the cubes are attached. Then you can build them yourself. You can find everything here.a

# How the cubes fit together


Make sure the cubes are properly stuck on the plate and
not tilted.
Tip: The cubes hold best in „sandwich“ format, with the
plates holding the cubes at the top and bottom

If you do not see a sharp image, move the inserts (e.g. lens) until you see it clearly.
The black arrow in the picture shows you how to do this.

# What a lens can do


Take one or more of the cubes that have a lens in them and look at the UC2 symbol shown here through it. Hold the cube in your hand and change the distance between the lens and the image.

Different lenses have different capabilities. What difference do you observe between the different lenses?

What does the picture look like?

Lenses; tion.; Converging lenses refract the light rays that run parallel to the optical axis at a point called the focal point.; Diverging lenses refract the light rays that run parallel to the optical axis as if they were ori- ginating from a point called the „virtual“ focal point.; The focal length of a lens here corresponds to the distance from the lens to the focal plane on which the focal point lies. It is given in millimetres (mm).; Positive Lens; In the „real“ world; On Paper; Focal point F‘ Positive Lens; Focal Plane; Focal Length f (positiv); Parallel rays; optical axis; „Focus“ F‘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

In ray optics, light is represented as a bundle of rays (arrows), which entails a simplification of the physical properties of light. A beam has a direction and is therefore drawn with an arrow. A lens „refracts“ the beam and thus changes its direc-

| With the diverging lens (f = - 50 mm) the image is always reduced

and always upright.

| | Have the answers raised any more questions? Then go on to find out how exactly the lenses work...

We assume that our lenses are so-called „thin lenses“. This means that we can look at them as a plane and not worry about their thickness. This makes explanations and calculations much easier.

The diverging lens is sometimes also called a negative or concave lens. The middle part of the lens is always thinner than the edge.

The image can be magnified with the converging lens. The magnification is different for the 50 mm lens and the 100 mm lens. The image can be upright or inverted.

The converging lens is also called a positive or convex lens. The middle part of the lens is always thicker than the edge.

# Lenses „refract“ the light rays

You will find the focal length of the lens as a printed number on the lens holders. The CoreBOX contains one 100 mm converging lens, two 50 mm converging lenses and one -50 mm diverging lens. The numbers indicate the focal length.

Imaging using a lens; focal length?; tance between the lens and the image?

Now take the lens cubes. Try to decipher the respective information about the focal length in the illustrated cubes with the matching lens. Move the lens over the writing until it is the same size as the text „UC2“ in the middle.

What happens if you get a lens with the wrong

Can you see the text the same size and orientation as the „UC2“? What happens when you change the dis-

# Imaging an object through a positive lens

Let‘s take the converging lens as an example. We start with an object (green arrow) and see what happens to the rays that start from the top. There are infinitely many rays in all directions, but for drawing the figure the following three rays will suffice:
1. The center ray (orange) passes undisturbed through the center of the lens.
2. The focal beam (yellow) also starts from the tip of the arrow, but goes through the object-side focal point at focal length f. After the lens, it continues at the same height, but now parallel to the optical axis.
3. The parallel beam (red) initially runs parallel to the optical axis, but is then refracted at the lens in such a way that it runs through the focal point on the image side at focal length f.
The image is formed where all the rays intersect. The principle is the same for all points or the rays of an object emanating from them. Depending on which lens is used and depending on the position of the object, the properties of the image change, such as size, orientation and position.
Focal length | Focal length

Parallel Ray

Focal Plane | Focal Plane

optical Axis

Focal Ray

Image

Lens

Center Ray

Object

# Imaging an object through a negative lens

Image; images.; Focal length; Focal plane; Object

In the case of the negative lens, we use the same method to image the ray path. Unlike the case of the converging lens,
the image is always reduced and virtual. Magnification depends on the position of the object in front of the lens. Unlike
the converging lens, the image is created on the object side and is therefore called a virtual image. You can see it directly
with your eyes but not project it onto a screen.

The way a lens creates an image is predictable by kno-
wing the focal length of that lens. Therefore, a certain
distance must be maintained so that you can see the
writing with the specified lens on the previous sheet.

With the diverging lens (f = -50 mm) you always see
a reduced virtual image. A virtual image can only be
viewed with the eye. So far we have only seen virtual

The magnification and the location where the image is
formed depend on the focal length of the lens and the
distance between the lens and the object.

The Positive lens as a magnifying glass; The magnifying glass..

Take the UC2 lens cube with focal length f = 50 mm and use it as a magnifying glass.

... is a simple converging lens with a small focal length.

Put the lens cube on the sheet and move the lens to a height

until you can read the text written here.

The magnifying glass is the simplest optical device!

Can you read the small letters through the converging lens? What is written there?

The Positive Lens; the lens, then the image is... • the opposite • swapped sides • scaled down • real; lens, then the image is... • the opposite • swapped sides • same size • real; image is... • the opposite • swapped sides • enlarged • real; Bild; Object; Image; Image width (b) The distance between the lens plane and the image formed by the lens is de- noted as b.; Object distance (g) The distance between the object and the lens plane is called g.; The converging lens can produce a real image. The real image can then be seen on a screen.

The magnification and position of the object depend on the converging lenses.

If the distance between the object and the lens is more than twice the focal length of

If the distance between the object and the lens is exactly twice the focal length of the

If the distance between the object and the lens is more than the focal length and less than twice the focal length of the lens, then the

# Why the positive lens magnifies

Lupeneffekt
If the distance between the object and the lens is less than
the focal length of the lens, then the image is...
• upright
• right orientation
• magnified
• virtual

Calculate the mangification of a lens using the follo-

The magnifying glass is the simplest of all optical devi-
ces, because it consists only of a simple converging lens
with a suitable focal length. Why does the cube with the
50 mm enlarge the small text? If the object is in front of
the focal length of the lens - i.e. less than 50 mm in front
of the lens - the lens creates a virtual image which is
behind the actual object. The eye perceives it enlarged.

250 mm is the distance of clear visual range - i.e. the
distance between the object and the eye at which
most people can read well. More on this later in the

Check out the diagram above.

“accommodation” of the eye.

# How does a movie projector work?

Illlumination; Positive lens 50mm; Object

Take the UC2 lens cube with a focal length of f = 50 mm and place it behind the sample holder cube. The distance bet-
ween the object and the lens (i.e. the object distance g) should be approx. 60 mm. If you now illuminate the object with
the flashlight, you will see it sharply at a distance of approx. 300 mm on the wall. A cinema projector has a film strip in-
stead of the object and of course a much stronger light source.

How is the image oriented?

Slide the lens back and forth in the cube and see when
the image is in focus. Find the image for g = 60 mm, 65
mm, 70 mm and measure the distance between the lens

Use a flashlight (e.g. from your mobile phone)
as a light source and hold it in front of the object.

and the image.

How does a movie projector work?; Where is the iamge?; How big is the image?; Focal lengthf; Distance to object; Distance to image; Bildgröße B; Distance to the object

When an object is imaged through a converging lens, the position and size of the image depend on the distance (g) of the object to the lens and its focal length (f).
The lens equation describes the relationship between image distance (b) and object distance (g):

The magnification of the object on the screen can easily be calculated using the following formula:

lation.; different values g and b.; Focallength f; Object size G; g Distance to the object; b Distance to the image; How does a movie projector work?; for g = 60 mm => b = 300 mm for g = 65 mm => b = 217 mm for g = 70 mm => b = 175 mm; Image size B

Check whether your observation agrees with the calcu-

Calculate the magnification of the projector for the

Our lens has a focal length of f = 50 mm.

The projector always produces an enlarged, inverted (reversed) image. The position of the image and its magnification depend on the position and size of the object.

This is a Galileo telescope; fObjektiv – fOkular; What does the picture look like? How is the image oriented?; Negative Lens -50mm; Ocular; Positive lens 100mm; Objective

Place the lens cubes on the sheet as shown in the diagram and then use the telescope to look into the distance.

As you look through the telescope, adjust the distances between the components to see a sharp image!x

# How does the Galileo telescope work?

A telescope is an optical instrument that makes distant objects appear many times closer or larger.

Die Linse auf der Ob-
jektseite nennt man
Objektiv.

The lens on the object side is
called the lens.

The Galileo telescope is also used in opera glasses.

# How does the Galileo telescope work?

Eyepiece; fOkular; Objective; fObjektiv

What is the magnification of this Galileo telescope?
Formula for calculating magnification

Field of view designates the area in the field of view of an optical device within which objects can be recorded.

The image is always
• magnified with the magnification from the formula
above
• upright
• true to side
The field of view is small.

It is not possible to achieve very high magnification
with this telescope. But it is very compact.

# What is the Kepler-Telescope?

put the lenses in the right position as shown in the diagram. Then look through the telescope into the distance.

What does the picture look like?
How is the image oriented?

As you look through the telescope, adjust the distances
between the components to see a sharp image!

# How does the Kepler-Telescope work?

Positive Lens; long focal length; short focal length; Objecitve; Eyepiece; fObjektiv; fOkular

This type of telescope is often used in astronomy.

# This is how the Kepler telescope works

What is the magnification of this Kepler telescope?
Formula for calculating magnification

The picture is always
- magnified with the magnification from the formula
above
- the opposite
- swapped sides
The field of view is larger than that of the Galileo tele-
scope.

This telescope can achieve a higher magnification
than the Galilean telescope. But it creates the opposite
picture. However, this is not a problem for observing the

# This is a spotting scope

The spotting scope is long, so the scheme here is not as big as in reality. Set the lenses in the correct position as shown
here and look into the distance through the telescope.

How does the image here compare to the Kepler tele-

As you look through the telescope, adjust the distances
between the components to see a sharp image!

# This is how the spotting scope works

Kepler telescope; Eyepiece; fOkular; 2xfUmkehrlinse; Positive lens; Objective; reversing lens; fObjektiv

This is the simplest spotting scope. The image is inverted compared to the Kepler telescope because that is better for
terrestrial observation. Once you understand the concept of the Keppler telescope and converging lens imaging, you can
easily combine them as shown here:

# This is how the spotting scope works

The magnifi-
cation is the
same as that
of the Kepler
telescope. The
erecting lens
only changes
the orientati-
on (the image
is reversed),
not the mag-

The picture is
• enlarged with the same magnification as with the
Keppler telescope
• upright
• true to side

An upright image is necessary for terrestrial observa-
tions. True terrestrial telescopes use prism systems to
rotate the image and keep it compact.

# Light microscope with „infinity optics“

empty; Positive lens 50mm; Positve lens 100mm; Objective; Illumination; fObjektiv + fTubuslinse; Tube lens; Image; Kepler-Telescope!; Object; fObjektiv; fTubuslinse

Place the object about 50 mm in front of the lens and find the image about 100mm behind the tube lens (using a paper
or the wall as a screen) as shown in the diagram. Move the lenses to get a sharp image.

What happens if you turn the Kepler telescope upside down?

Place the object with the lens together as one unit on the paper. Set up the tube lens at a distance of 100 mm from

your screen. Change the distance between the lenses - does the image change?

# What means „infinity optics“?

Objective; Tube lens; Object; Intermediate image; fObjektiv; fTubuslinse

A microscope is a device that allows objects to be viewed or imaged at high magnification.

The image is called an interme-
diate image because it is often
further enlarged with an eyepiece.

The tube lens creates a real image
by collecting parallel rays that
strike the tube lens in its focal
plane. If we place them behind the
lens, the object will be imaged from
the focal plane of the lens. The
tube lens has a longer focal length

The object is approximately in the
object-side focal plane of the lens.
Thus, all incident rays are conver-
ted into a parallel bundle of rays
behind the lens. The lens has a
short focal length.

The image in the plane of the
intermediate image is reversed,
flipped, enlarged and real. The real
image can be seen on a screen.

than the objective.

# What means „infinity optics“?

A microscope is a device that allows objects to be viewed or imaged at high magnification.

What is the magnification of the image?

Objectiv Tube lens

The lenses of the Kepler telescope can also be used for a microscope, but in a different order. As long as the object is
in the focal plane of the lens and the screen is in the focal plane of the tube lens, the distance between the lens and

the tube lens doesn‘t matter because the light rays are parallel.

# „Infinity optics“ with eyepiece

sharp image!; Illumination; Objective; Tube lens; Object; Eyepiece; Intermediate iamge; piece.; empty; Positive lens 50mm; Positive lens 100mm; Positive; lens; Mirror

The setup below shows an entire microscope. Place the dice in the positions shown in the diagram.
The intermediate image is imaged behind the mirror through an eyepiece.
What do you see when you look through?

Build the microscope like a sandwich by ad-
ding a second layer using a base plate. Look
through the eyepiece from above.

As you look through the microscope, adjust
the distances between components to get a

Can you see the microscopic image through the eyepiece lens with your eyes? What effect does the mirror have? Set
up the microscope without the mirror. Make sure you still have two empty spaces between the tube lens and the eye-

The eyepiece is used for...

Objective; Tube lens; Object; fObjektiv; fTubuslinse; fOkular; Eyepiece; Intermediate image

Newer microscopes are equipped with so-called „infinity optics“. In this case, the lens does not produce a real interme-
diate image. The light exits the lens as infinite parallel rays. At the end of the „infinite“ tube is a tube lens. This creates an
intermediate image, which is then enlarged again through the eyepiece.

A filter can be used to change the brightness and color

„infinite“ tube length, which can be arbitrarily large or small

of the image.

The image behind the eyepiece is reversed, reversed, enlarged and virtual. The virtual image can be seen with the eye.
This configuration is very useful in modern microscopes as it allows additional components such as filters to be placed

between the objective and tube lens without affecting the optical path.

The eyepiece is used for...

Newer microscopes are equipped with so-called „infinity optics“. In this case, the lens does not produce a real interme-
diate image. The light exits the lens as infinite parallel rays. At the end of the „infinite“ tube is a tube lens. This creates an
intermediate image, which is then enlarged again through the eyepiece.

What is the magnification after the eyepiece?

An eyepiece is actually just a lens
that enlarges the intermediate
image. It maps the virtual image
in such a way that you can see it

with your eyes.

With the mirror you can not only
see yourself, but also reflect the
incoming light in any direction.
So you can fold the optical path
and make it more comfortable
to work with. The mirror doesn‘t
affect the magnification, but it
does rotate the image in one

„infinite“ tube length, which can also be arbitrarily large or

# Light microscope with „finite optics“

Mirror; of paper?; Positive lens; Objective Object; Illumination; Eyepiece; Intermediate Image; empty

Place the dice in the positions shown in the diagram below and look through the eyepiece.

Build the microscope like a sandwich by adding a second layer using a
The lens can be moved back and forth in the linear stage.

base plate. Look through the eyepiece from above.

Do you see the image through the eyepiece as before?
Can you find the real intermediate image with a sheet

Turn the small gear on the lens holder. This is how you
move or focus the lens. If you can‘t go any further, you

can also move the lens in the holder.

# „Finite optics“ versus „Infinite optics“

Object; Objective; Intermediate Image; Eyepiece; fObjektiv; fOkular defined tube length of the finite objective

The lenses of older or smaller microscopes are often so-called finite lenses. They behave like a lens with an extremely
short focal length and create an intermediate image behind the lens with an image distance that is defined by the tube
length. The tube length is printed and corresponds to 160 mm for our lens. The real intermediate image is created there
and is enlarged by the eyepiece optics.

Microscopes have the ability to focus or sharpen the object either by moving the object or the lens.
Here we simply move the lens holder by hand. We adjust the distances between the components to see a sharp image.

# „Finite optics“ versus „Infinite optics“

What is the magnification of the intermediate image? And what is the magnification after the eyepiece?
lens magnification

as written on it

The image is larger than with the
infinity microscope. The magnifi-
cation of the lens here is 4x. If you
calculated the magnification with
the previous microscope, this cer-
tainly doesn‘t surprise you.

The intermediate image is now
only formed by the lens and is 160
mm behind it. We‘ll find out why in

defined tube length of the finite objective

the next step.

Das Objektiv ist auch eine Sammellinse mit kurze Brennweite.

4/0.10
160/0.17

2 x converging
lens 50 mm

Look through the single 50 mm lens and then through the dual lens at the grid.

Look through the 50 mm lens and then look through the lens at the small text.

Which of the lenses magnifies more? what stands
written there? | How does the magnification and field of view change?

# Objective and eyepiece

Open the cubes with the 50 mm lenses. Now place both 50 mm lenses in a cube so that the „bellies“ of the lenses are pointing at each other.

Look at the lens! What‘s in there? what is written on it

4/0.10
160/0.17

# This is the objective lens

An objective is an optical system or assembly that produces a magnified image of an object. The different numbers imprinted on the objective have different meanings:

Coverslip correction :
A coverslip is sometimes used to seal the sample. A lens must be corrected for this thickness (0.17 mm).

Numerical Aperture:
It determines the ability to collect light and thus the optical resolution.

Tube length:
∞ stands for infinity, 160 stands for 160 mm and is the most commonly used tube length according to DIN

Magnification:
Common magnifications
are 4x, 10x, 40x, 100x.

The 4x objective has only one lens in it. The higher magnification lenses are complete lens systems.

The lens is also a converging lens with a short focal length. The 4 x lens has a focal length of f = 32 mm. When used as a magnifying glass, it has a higher magnification than the 50 mm lens. The field of view is sharp but small.

# This is the eyepiece

An eyepiece is actually a magnifying glass because it enlarges the intermediate image. The eyepiece we use here is a so-cal-
led Ramsden eyepiece.
A single lens can also be used as an eyepiece. However, with the Ramsden eyepiece, which consists of a lens system, the field
of view is better because it produces fewer errors at the edge of the field of view. The Ramsden eyepiece consists of two len-
ses with the same focal length. Its focal length is fRamsden-Okular= 3/4 fLinse

What is the magnification of the Ramsden eyepiece?

The image scale is higher at short object distances than

with a single 50 mm lens.

Each eyepiece has a so-called Ramsden disk, which is
the smallest diameter of the light beam that exits the

The field of view is larger and the image looks clearer

with the Ramsden eyepiece.

microscope through the eyepiece.

# Smartphone Mikroskop

Mirror; Ramsden-Eyepiece; Object; Illumination

Build the smartphone microscope as shown. Use any two cubes to
safely place the smartphone.

or smartphone ca-
mera
Alternatively:
Use Eyepiece

Build the microsco-
pe like a sandwich
by adding a se-
cond layer using a
base plate. Look
through the eye-
piece from above.

This Cube is
optional

Replace the
Ramsden eye-
piece with the
50 mm lens.
What is better
for the eye and
what for the
smartphone?

# Better with smartphone or eye?

accommodation; Autofocus

The smartphone camera has a lens with a very short focal length because it has to fit into the thin smartphone. The lens then
creates an image on the camera sensor whose properties are similar to the human eye.

The eye can depict objects both from a distance and from close up. This property is called accommodation.
The smartphone camera can also do this, but it is called autofocus. It describes the ability to move objects into

different distances sharply on the sensor.

The image from the eyepiece comes in parallel rays, as if coming from infinity. It was observed with a relaxed eye (loo-

king into the distance) or with a camera focused at infinity.

# Better with smartphone or eye?

In order to be able to see the image of the microscope, the pupil - i.e. the „aperture“ that limits the incidence of light - must
match the Ramsden disc of the eyepiece. The pupil of the eye is fixed inside and cannot be brought closer to the eyepiece. The
pupil of the smartphone camera, on the other hand, is very close to the surface of the cell phone. Because of this difference,
you need a different distance to the eyepiece for the eye and the camera.

What is the magnification of this microscope?
Formula for calculating magnification

With the Ramsden eyepiece, the Ramsden disc is closer
to the cube and has a smaller diameter, which works

well for the smartphone camera.

pupil of the eye

The Ramsden disk of the single 50 mm lens has a larger
diameter, making it more convenient for observing the
sample with the eye. Through the eyepiece it looks as if
the image is on the mirror underneath. The 50 mm len-
ses have a large diameter, so when using a single lens
as an eyepiece, the field of view is limited by the size of

pupil of the camera

Lupe; Projektor; Galilei-Fernrohr; Kepler-Fernrohr; „Unendlich“-Mikroskop; „Unendlich“-Mikroskop mit Okular; „Endlich“-Mikroskop - Zwischenbild; Ramsden-Okular; Smartphone Mikroskop mit Ramsden-Okular; Calculation results

## „Endlich“-Mikroskop - Gesamtvergrößerung

# Glossary

Beam of light
An arrow or line showing the direction of the light; Unless otherwise stated, the light in the schemes always comes from the left.
Lens
A transparent refractive body z. B. made of glass or plastic Thin lens
A model of a lens that assumes it has no volume Converging lens
A lens that converges (collects) the incoming light Diverging lens
A lens that fans out the incoming light
Focus F (object focus), F‘ (image focus)
A point where light is focused (collecting lens) or from which it appears to diverge (diverting lens)
Focal length f
The distance between the focal point & the thin lens Focal plane
A plane parallel to the thin lens that passes through the focal point
Optical axis
The basic framework for every optical sketch; it passes through the center of the lens and is perpendicular to the plane of the lens
virtual image
An image produced by a lens or optical system that can be viewed by a human eye through the system
real picture
An image produced by a lens or optical system that can be viewed on a screen behind the system
Magnification
A ratio of the image size and the object size (for a real image); a ratio of the observed image and the object size (for a virtual image)
Object
An object that we want to image with the lens; the size of the object is G
Distance g of the object
The distance between the object and the thin lens
Image
An image of the item; Size of the picture is B.
Distance (b) of the image
The distance between the image (real or virtual) and the thin lens

Object page
side in relation to the lens on which the object (item) is located; left in the schemes
Image side
side relative to the lens on which the real image is formed; The virtual image is on the same side as the object. Center ray
Center rays pass through the thin lens unchanged. Parallel rays
All rays that run parallel to the optical axis are refracted by the lens in such a way that they meet at the focal point. As the brightest point directly behind the lens, this is only found in converging lenses.
Focal rays
All rays that pass through a focal point or come out of the focal point are refracted by the lens in such a way that they pass parallel to the optical axis behind the lens. Illumination
In microscopy, you need an illumination source to be able to see the object. This can e.g. B. a flashlight or the reflection from the sun.
Magnifying glass (also magnifying glass or burning glass) The simplest optical device that magnifies the object for the human eye
Telescope (also lens telescope or refractor)
An optical instrument that, when used, makes distant objects appear many times closer or larger

Lens
An optical system that creates a real optical image of an object
Eyepiece
The eye-side part of an optical system
Light microscope
A microscope that uses light to produce highly magnified images of small structures or objects
Tube lens
A lens that creates a real intermediate image from the parallel rays of light after the infinity optics lens
Intermediate image
Magnifying image of the object produced by the lens Mirror
A reflective surface smooth enough for light reflected off it to create an image
Accommodation of the eye
A dynamic adjustment of the refractive power of the eye; It means that objects at different distances can be imaged sharply on the retina.
Autofocus
Unlike accommodation, in most cases of autofocus, the focal length remains constant and the distance between the lens and the screen is varied.

# Impressum

Productdesign: Barbora Maršíková, Benedict Diederich

Layout: Katrin Uhlig, Benedict Diederich www.openUC2.com

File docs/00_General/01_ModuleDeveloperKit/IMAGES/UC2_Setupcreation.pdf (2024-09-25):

Tholabs

Mirror

Dichroic

Kinematic
Mirror

CAM

Sample Holder

Beamexp.

BS

Lens

Laser Holder

Eyepiece

Z-stage

S-stage | Sample Holder - comb

LED

LED
Array

Kinematic
Mirror

Cellphone

# Toolbox of available UC2-Parts

# Playground for optical setups

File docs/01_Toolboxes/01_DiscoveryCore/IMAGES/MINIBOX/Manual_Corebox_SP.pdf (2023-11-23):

# CoreBOX

# UC2 Handbuch

Bitte beziehen Sie sich immer auf die www.openuc2.com bzw. www.openuc2.github.io für eine aktualisierte Version dieses Handbuchs.
Übersetzte Versionen des Handbuchs sind verfügbar unter: Englisch: https://openuc2.github.io/docs/Toolboxes/DiscoveryCore/ENGLISH/uc2miniboxEN
Deutsch: https://openuc2.github.io/docs/Toolboxes/DiscoveryCore/GERMAN/uc2miniboxDE

Lesen Sie sorgfältig! Dieser Teil des Textes hat die größte Bedeutung - entweder für die Sicherheit der Benutzer oder für die ordnungsgemäße Wartung der Optik-Komponenten. Diese Informationen beziehen sich auf die OpenUC2 CoreBox, die Discovery Electronics(+) und Discovery Interference.

So erreichen Sie den technischen Support von OpenUC2: Schauen Sie zunächst in den letzten Kapiteln dieses Handbuchs nach Anleitungen zur Fehlerbehebung oder besuchen Sie forum.openuc2.com für eine vollständige Liste der häufigsten Probleme, der Fehlerbehebung und anderer Anleitungen. Die Dokumentationswebsite openuc2.github.io bietet weitere Informationen für die mögliche Verwendung des Produkts.
Wenn Ihr Problem dort nicht aufgeführt ist oder die Lösung nicht funktioniert, senden Sie bitte eine E-Mail an support@ openuc2.com. Versuchen Sie, Ihr Problem so gründlich wie möglich zu erklären - Fotos und/oder Videos anhängen, wenn möglich.

Handbuch Version 0.1 vom 8. November 2023, openUC2 GmbH

Informationen über Funktionalität, korrekte Verwendung und Wartung der Komponenten finden Sie in diesem Handbuch und online unter support.openuc2.com.

Soweit vorhanden, muss das Gerät von der Stromversorgung (Netzteil) getrennt werden, bevor irgendeine Art von Service durchgeführt wird, andernfalls riskieren Sie möglicherweise eine elektrische Verletzung. Lesen Sie das Handbuch und die Wissensdatenbank unter support.openuc2. com, bevor Sie Wartungsarbeiten am Gerät durchführen.


# ¿Qué hay dentro?

Mikroskopobjektiv; Lente positiva 50 mm; Lente positiva 100 mm; Sample holder; Lente negativa; Espejo; Etapa lineal; Lente objetivo (4x); Ocular (10x); Antor

Portamuestras y platina lineal:
Sujeta la muestra y mueve el objetivo
Espejo,lente, ocular y objetivo:
Enfoca y refleja

Atención:
No toque el cristal.
Limpieza de las lentes: Utilice
un paño de limpieza de lentes

Cubo

Cubo (Mitad)

Inserto (por ejemplo,

Cubo (Mitad)

Placa base

# You.See.Too.? UC2!

El elemento central del proyecto UC2 es un simple cubo. El cubo consta de dos mitades y alberga un inserto deslizante. El inserto puede alojar distintos componentes ópticos (por ejemplo,lentes o espejos),lo que permite realizar diferentes funciones con cada cubo. Los cubos, así como las placas base en formato puzzle, que pueden extenderse en todas las direcciones, se moldean por inyección y, por tanto, tienen una gran precisión. Las piezas se mantienen en su sitio mediante un ajuste positivo, lo que elimina la necesidad de magnetos y tornillos. Los insertos en formato de placa de tope pueden adaptarse rápidamente a nuevos componentes y encontrar espacio en el cubo.

# Cubo Tipo 1

Moldeado por inyección con Formfit

El cubo puede montarse sobre una placa base. Los módulos de la placa base pueden unirse como un rompecabezas

Placa base

portamuestras)

Placa base con imanes

# UC2 para impresión 3D DIY

Además del diseño moldeable por inyección, el cubo también está disponible en versión imprimible. Ambos cubos son compatibles entre sí, pero el cubo formado por tapa y cuerpo es más fácil de imprimir. Los tornillos magnéticos se utilizan para conectar a los imanes esféricos de la placa. Combinando diferentes módulos de cubo, es muy fácil montar diferentes estructuras ópticas. Con cada cubo se puede añadir una nueva función. La creatividad no tiene límites.

# Cubo Tipo: 2

Impreso en 3D con conexión magnét-

Place base

Cubo

Cubo (Cuerpo)

Tornillo (magnético)

Ballmanget

Cuerpo (Tapa)

En la placa base impresa en 3D se incrustan pequeños imanes esféricos sobre los que se fijan los cubos. Así podrás construirlos tú mismo. Puedes encontrarlo todo aquí

# Cómo encajan los cubos


Asegúrese de que los cubitos están bien pegados a la
placa y no inclinados.
Consejo: Los cubos se sujetan mejor en formato „sandwich“, con las placas sujetando los cubos arriba y

Si no ve una imagen nítida, mueva los insertos (por ejemplo, el objetivo) hasta que la vea con claridad. La flecha verde de la imagen muestra cómo hacerlo.

# Lo que una lente puede hacer


Coge uno o varios de los cubos que tienen una lente y mira a través de ellos el símbolo UC2 que se muestra aquí. Sujeta el cubo con la mano y cambia la distancia entre la lente y la imagen.

Los distintos objetivos tienen capacidades diferentes. Qué diferencias observas entre las distintas lentes?

¿Qué aspecto tiene la imagen?

Lentes; cambia su dirección; Las lentes colectivas refractan los rayos luminosos que viajan paralelos al eje óptico en un punto denominado punto focal.; Las lentes divergentes refractan los rayos de luz que discurren paralelos al eje óptico como si estuvieran ori- ginando desde un punto llamado el punto focal „virtual“.; La distancia focal de una lente corresponde aquí a la distancia de la lente al plano focal en el que se encuentra el punto focal. Se expresa en milímetros (f = mm).; Lente positiva; En el mundo „real“; Sobre el papel; Fokus – Brennpunkt F‘; Lente; positiva; Focal Plane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

En la óptica de rayos, la luz se representa como un haz de rayos (flechas), lo que supone una simplificación de las propiedades físicas de la luz. Un rayo tiene una dirección y, por tanto, se dibuja con una flecha. Una lente „refracta“ el rayo y

Con la lente divergente (f =- 50 mm) la imagen es siempre
reducida y siempre vertical.

¿Le han surgido más preguntas? Averigüe cómo funcionan exactamente las lentes...

Suponemos que nuestras lentes son las llamadas „lentes delgadas“. Esto significa que podemos verlas como un plano y no preocuparnos por su grosor. Esto facilita mucho las explicaciones y los cálculos.

La lente divergente (lente negativa) a veces también se denomina lente negativa o cóncava. La parte central de la lente es siempre más delgada

La imagen puede ampliarse con el objetivo convergente. La ampliación es diferente para el objetivo de 50 mm y el de 100 mm. La imagen puede estar en posición vertical o invertida.

La lente convergente también se denomina lente positiva o convexa. La parte central de la lente es siempre más gruesa que el borde.

# Las lentes „refractan“ los rayos de luz

Encontrará la distancia focal del lente objetivo como un número impreso en los portaobjetivos. La CoreBOX contiene un objetivo convergente de 100 mm, dos objetivos convergentes de 50 mm y un objetivo divergente de -50 mm. Los números indican la distancia focal.

Tomar imágenes con una lente; „UC2“ del centro.; distancia focal equivocada?; entre el objetivo y la imagen?

Ahora coge los cubos de las lentes. Intenta descifrar la información correspondiente sobre la distancia focal en los
cubos ilustrados con la lente correspondiente. Mueve la lente sobre lo escrito hasta que tenga el mismo tamaño que el texto

¿Qué ocurre si se adquiere un objetivo con la

¿Puedes ver el texto del mismo tamaño y orientación que el „UC2“? ¿Qué ocurre si cambias la distancia

# Imagen de un objeto a través de una lente positiva

Tomemos como ejemplo la lente convergente. Empezaremos con un objeto (flecha verde) y veremos qué ocurre con los rayos que parten de la parte superior. Hay infinitos rayos en todas las direcciones, pero para dibujar la figura bastarán los tres rayos siguientes:
El rayo central (naranja) atraviesa imperturbable el centro de la lente.
El haz focal (amarillo) también parte de la punta de la flecha, pero atraviesa el punto focal del lado del objeto a la distancia focal f. Después de la lente, continúa a la misma altura, pero ahora paralelo al eje óptico.
El haz paralelo (rojo) discurre inicialmente paralelo al eje óptico, pero luego se refracta en la lente de tal forma que atraviesa el punto focal por el lado de la imagen a la distancia focal f.
La imagen se forma donde se cruzan todos los rayos. El principio es el mismo para todos los puntos o los rayos de un objeto que emana de ellos. Dependiendo de la lente que se utilice y de la posición del objeto, cambian las propiedades de la imagen, como el tamaño, la orientación y la posición.
Focal length | Focal length

Parallel Ray

Focus | Focalplane

optische Achse

Focal Ray

Image

Lens

Center Ray

Object

# Imagen de un objeto a través de una lente negativa

En el caso de la lente negativa utilizamos el mismo método para obtener la imagen de la trayectoria del rayo. A diferen-
cia del caso de la lente convergente, la imagen es siempre reducida y virtual. La ampliación depende de la posición del
objeto delante de la lente. A diferencia de la lente convergente, la imagen se crea en el lado del objeto, por
lo que se denomina imagen virtual. Se puede ver directamente con los ojos, pero no proyectarla en una pantalla.

La forma en que un objetivo crea una imagen se puede
predecir conociendo su distancia focal. Por lo tanto,
hay que mantener una cierta distancia para
poder ver lo escrito con el objetivo especificado en la

Con la lente divergente (f =-50 mm) siempre se ve una
imagen virtual reducida. Una imagen virtual sólo puede

verse con el ojo. Hasta ahora sólo
hemos visto imágenes virtuales.

El aumento y el lugar donde se forma la imagen de-
penden de la distancia focal del objetivo y de la distan-

cia entre el objetivo y el objeto.

La lente positiva como lupa; La lupa..; puedas leer el texto escrito aquí.

Toma el cubo de lentes UC2 con distancia focal f =50 mm y utilízalo como lupa.

...es una simple lente convergente con una distancia focal pequeña.

Coloca el cubo de lentes sobre la hoja y desplázalo a una altura tal que

¿Puede leer las letras pequeñas a través de la lente convergente? ¿Qué hay escrito?

f

f

f

f

# La lente positiva

El aumento y la posición del objeto dependen de las lentes convergentes.

- Si la distancia entre el objeto y el objetivo es superior al doble de la distancia focal del objetivo, la imagen es...
- Invertida
- Del otro lado
- Reducida
- Real
- Si la distancia entre el objeto y el objetivo es exactamente el doble de la distancia focal del objetivo, entonces la imagen es ...
- Invertida
- Del otro lado
- Del mismo tamaño
- Real
- Si la distancia entre el objeto y el objetivo es mayor que la distancia focal y menor que el doble de la distancia focal del objetivo, entonces la imagen es...
- Invertida
- Del otro lado
- Ampliada
- Real

Bild

Object

Object | Image
2xf | f | f | 2xf
g | b

Anchura de imagen (b)
La distancia entre el plano de la lente y la imagen
formada por la lente se
denomina b.

Distancia al objeto (g)
La distancia entre el objeto y el plano de la lente se denomina g.

La lente convergente puede producir una
imagen real. La imagen
real puede verse en una
pantalla.

2xf

2xf

2xf

2xf

# Por qué la lente positiva aumenta

siguiente lente:; La lupa es el más sencillo de todos los dispositivos óp-; Distnace to object; Distance to image

Efecto Lupen
Si la distancia entre el objeto y el objetivo es inferior a la
distancia focal del objetivo, la imagen es ...
• Vertical
• Del mismo lado
• Ampliada
• virtual

Calcular la mangificación de una lente utilizando la

ticos, porque sólo consiste en una simple lente conver-
gente con una distancia focal adecuada. ¿Por qué el
cubo de 50 mm amplía el texto pequeño? Si el
objeto se encuentra delante de la distancia focal de la
lente, es decir, a menos de 50 mm delante de la lente,
ésta crea una imagen virtual que se encuentra detrás
del objeto real. El ojo lo percibe ampliado.
Echa un vistazo al diagrama anterior.

250 mm es la distancia de alcance visual claro, es
decir, la distancia entre el objeto y el ojo a la que la
mayoría de las personas pueden leer bien. Más ade-
lante hablaremos de la „acomodación“ del ojo.

# ¿Cómo funciona un proyector de cine?

Tome el cubo de objetivo UC2 con una distancia focal de f =50 mm y colóquelo detrás del cubo portamuestras. La dis-
tancia entre el objeto y el objetivo (es decir, la distancia del objeto g) debe ser de unos 60 mm. Si ahora ilumina el objeto
con la linterna, lo verá nítidamente a una distancia de aprox. 300 mm en la pared. Un proyector de cine tiene una tira de
película en lugar del objeto y, por supuesto, una fuente de luz mucho más potente.

¿Cómo está orientada la imagen?

Desliza la lente hacia adelante y hacia atrás en el cubo
y observa cuándo está enfocada la imagen.
Encuentra la imagen para g =60 mm, 65 mm, 70 mm y
mide la distancia entre la lente y la imagen.

Utiliza una linterna (por ejemplo, la de tu teléfono mó-
vil) como fuente de luz y mantenla frente al objeto.

¿Cómo funciona un proyector de cine?; ¿Dónde está la imagen; (b) y la distancia del objeto (g):; ¿Qué tamaño tiene la imagen?; Focal lengthf; Distance to object; Distance to image; Bildgröße B; Distance to the object

imagen dependen de la distancia (g) del objeto a la lente y de su distancia focal (f). La ecuación de la lente describe la relación entre la distancia de la imagen

El aumento del objeto en la pantalla puede calcularse fácilmente mediante la siguiente fórmula:

gg = BB GG diferentes valores g y b; Focallength f; Object size G; g Distance to the object; b Distance to the image; ¿Cómo funciona un proyector de cine?; Nuestro objetivo tiene una distancia focal de f =50 mm. para g =60 mm =>b =300 mm para g =65 mm =>b =217 mm para g =70 mm =>b = 175 mm; de la posición y el tamaño del objeto.; Image size B

Comprueba si tu observación coincide con el cálculo.

Calcular el aumento del proyector para el

El proyector produce siempre una imagen ampliada e invertida. La posición de la imagen y su ampliación dependen

Este es un telescopio Galileo; lo lejos.; fObjektiv – fOkular; ¿Qué aspecto tiene la imagen? ¿Cómo está orientada la imagen?; componentes para ver una imagen nítida!; Negative Lens -50mm; Ocular; Positive lens 100mm; Objective

Coloca los cubos de lentes en la hoja como se indica en el diagrama y, a continuación, utiliza el telescopio para mirar a

Al mirar por el telescopio, ajusta las distancias entre los

# ¿Cómo funciona el telescopio Galileo?

Positive lens; Negative lens; long focal length; short focal length; parallel ray; Parallelstrahlen; Objektiv; Eyepiece; fObjektiv; fOkular

Un telescopio es un instrumento óptico que hace que los objetos lejanos parezcan muchas veces más cercanos o más
grandes.

La lente del lado del objeto se
denomina objetivo.

The Galileo telescope is also used in opera glasses.

# ¿Cómo funciona el telescopio Galileo?

Eyepiece; fOkular; Objective; fObjektiv

¿Cuál es el aumento de este telescopio Galileo?

Fórmula para calcular el aumento

El campo de visión designa la zona del campo de visión, valga la redundancia, de un dispositivo óptico dentro del cual se
pueden registrar objetos.

La imagen es siempre:
aumentada con el aumento de la fórmula anterior
vertical
de lado
El campo de visión es pequeño.

Con este telescopio no es posible conseguir grandes

aumentos. Pero es muy compacto.

# ¿Qué es el telescopio Kepler?

Coloca las lentes en la posición correcta, tal como se indica en el diagrama. A continuación, mira a lo lejos a través del

¿Qué aspecto tiene la imagen?
¿Cómo está orientada la imagen?

Al mirar por el telescopio, ajusta las distancias entre los
componentes para ver una imagen nítida.

# ¿Cómo funciona el telescopio Kepler?

Positive Lens; long focal length; short focal length; Objecitve; Eyepiece; fObjektiv; fOkular

Este tipo de telescopio se utiliza a menudo en astronomía.

# Así funciona el telescopio Kepler

¿Cuál es el aumento de este telescopio Kepler?
Fórmula para calcular el aumento

La imagen es siempre
-aumentada con el aumento de la fórmula anterior
opuesta
del otro lado
El campo de visión es mayor que el del telescopio Gali-
leo.

Este telescopio puede alcanzar un aumento mayor
que el telescopio galileano. Pero crea la imagen opu-
esta. Sin embargo, esto no es un problema para obser-

var el estrellas.

# Este es un telescopio terrestre

telescopio Kepler?; fObjektiv + 2xfUmkehrlinse; 2xfUmkehrlinse + fOkular; reversing lens; Positive lens 100mm; Positive lens 50mm; Objective; Eyepiece; empty; Positive Lens 50mm

El catalejo es largo, por lo que el esquema aquí no es tan grande como en la realidad. Coloca las lentes en la posición
correcta, como se muestra aquí, y mira a lo lejos a través del telescopio.

¿Cómo se compara esta imagen con la del

Al mirar por el telescopio, ajusta las distancias entre los
componentes para ver una imagen nítida.

# Así funciona el telescopio terrestre

Se trata del telescopio terrestre más sencillo. La imagen está invertida en comparación con el telescopio Kepler, ya que
es mejor para la observación terrestre. Una vez que comprenda el concepto del telescopio Keppler y la imagen de lente
convergente, podrá combinarlos fácilmente como se muestra aquí:

# Así funciona el telescopio

Umkehrlinse; fOkular 2xfUmkehrlinse; 2xfUmkehrlinse; Objektiv; Okular; fObjektiv; mantenerla compacta.

El aumento
es el mismo
que el del
telescopio
Kepler. La
lente erectora
sólo cambia
la orientación
(la imagen se
invierte), no el
aumento.

• La imagen es
• ampliada con el mismo aumento que con el telesco-
pio Keppler
• vertical
• de lado

La imagen vertical es necesaria para las observacio-
nes terrestres. Los verdaderos telescopios terrestres
utilizan sistemas de prismas para girar la imagen y

# Microscopio óptico con „óptica infinita”

Coloque el objeto a 50mm en frente del lente y encuentre la imagen a 100 mm detrás del lente tubular (usando papel o
una pared como pantalla), como se muestra en el diagrama. Mueva el lente para generar una imagen nítida.

¿Qué ocurre si se da la vuelta al telescopio Kepler?

Coloca el objeto con la lente juntos como una unidad sobre el papel. Coloca la lente tubular a una distancia de 100

mm de la pantalla. Cambia la distancia entre las lentes: ¿cambia la imagen?

# ¿Qué significa „óptica infinita”?

Objective; Tube lens; Object; Intermediate image; fObjektiv; fTubuslinse; focal corta.; objetivo.; pantalla.

Un microscopio es un dispositivo que permite ver o visualizar objetos con gran aumento.

La imagen se denomina imagen
intermedia porque a menudo se
amplía con un ocular.

La lente tubular crea una imagen
real recogiendo los rayos paralelos
que inciden sobre la lente tubular
en su plano focal. Si los colocamos
detrás de la lente, el objeto recibi-
rá la imagen desde el plano focal
de la lente. La lente tubular tiene
una distancia focal mayor que el

El objeto se encuentra aproxi-
madamente en el plano focal del
lado del objeto de la lente. Así,
incidentes convergen en un haz
de rayos paralelos detrás de la
lente. La lente tiene una distancia

La imagen en el plano de la ima-
gen intermedia se invierte, se vol-
tea, se amplía y se hace real. La
imagen real puede verse en una

todos los rayos

# ¿Qué significa „óptica infinita”?

Un microscopio es un dispositivo que permite ver o visualizar objetos con gran aumento.

¿Cuál es el aumento de la imagen?

Objectiv Tube lens

Las lentes del telescopio Kepler también pueden utilizarse para un microscopio, pero en un orden diferente. Mientras
el objeto esté en el plano focal de la lente y la pantalla esté en el plano focal de la lente del tubo, la distancia entre

la lente y la lente del tubo no importa porque los rayos de luz son paralelos.

# „Óptica infinita“ con ocular

Illumination; Objective; Tube lens; Object; Eyepiece; Intermediate iamge; empty; Positive lens 50mm; Positive lens 100mm; Positive; lens; Mirror

El siguiente montaje muestra un microscopio completo. Coloque los dados en las posiciones indicadas en el diagrama.
La imagen intermedia se visualiza detrás del espejo a través de un ocular.
Construye el microscopio como un
sándwich añadiendo una segunda capa uti-
lizando una placa base. Mira por el
ocular desde arriba.

Al mirar por el microscopio, ajusta las dis-
tancias entre los componentes para obtener

una imagen nítida.

¿Puede ver con sus ojos la imagen microscópica a través de la lente del ocular? ¿Qué efecto tiene el espejo? Monta
el microscopio sin el espejo. Asegúrate de que sigues teniendo dos espacios vacíos entre la lente del tubo y el ocular.

El ocular se utiliza para...

Objective; Tube lens; Object; fObjektiv; fTubuslinse; fOkular; Eyepiece; Intermediate image

Los microscopios más modernos están equipados con la llamada „óptica infinita“. En este caso, el objetivo no produce
una imagen intermedia real. La luz sale del objetivo en forma de rayos paralelos infinitos. En el extremo del tubo „infinito“
se encuentra una lente tubular. Ésta crea una imagen intermedia, que se amplía de nuevo a través del ocular.

Se puede utilizar un filtro para cambiar el brillo y el

„infinite“ tube length, which can be arbitrarily large or small

color de la imagen.

La imagen detrás del ocular es invertida, aumentada y virtual. La imagen virtual puede verse con el ojo.
Esta configuración es muy útil en los microscopios modernos, ya que permite colocar componentes adicionales, como

filtros, entre el objetivo y la lente tubular sin afectar a la trayectoria óptica.

El ocular se utiliza para...

Los microscopios más modernos están equipados con la llamada „óptica infinita“. En este caso, el objetivo no produce
una imagen intermedia real. La luz sale del objetivo en forma de rayos paralelos infinitos. En el extremo del tubo „infinito“
se encuentra una lente tubular. Ésta crea una imagen intermedia, que se amplía de nuevo a través del ocular.

¿Cuál es el aumento tras el ocular?

En realidad, un ocular no es más
que una lente que amplía la ima-
gen intermedia. Mapea la imagen
virtual de forma que puedas verla

con tus ojos.
Con el espejo no sólo puede
verse a sí mismo, sino también
reflejar la luz entrante en cu-
alquier dirección. Así puedes
doblar el camino óptico y
trabajar más cómodamente con
él. El espejo no afecta al au-
mento, pero sí gira la imagen en

„infinite“ tube length, which can also be arbitrarily large or

# Microscopio óptico con „óptica finita”

Mirror; Positive lens; Objective Object; Illumination; Eyepiece; Intermediate Image; empty

Coloca los dados en las posiciones indicadas en el diagrama siguiente y mira por el ocular.
Construye el microscopio como un sándwich añadiendo una segunda capa
La lente puede moverse hacia delante y hacia atrás en la etapa lineal.

utilizando una placa base. Mira por el ocular desde arriba.

¿Ves la imagen a través del ocular como antes?
¿Puedes encontrar la imagen intermedia real con una

Gire el pequeño engranaje del soporte del objetivo. Así
se mueve o enfoca el objetivo. Si no puedes ir más le-
jos, también puedes mover el objetivo en el soporte.

hoja de papel?

# „Óptica finita“ frente a „Óptica infinita“

Las lentes de los microscopios más antiguos o pequeños suelen ser las denominadas lentes finitas. Se comportan
como un objetivo con una distancia focal extremadamente corta y crean una imagen intermedia detrás del objetivo con
una distancia de imagen que viene definida por la longitud del tubo. La longitud del tubo está impresa y corresponde a
160 mm para nuestro objetivo. La imagen intermedia real se crea allí y es ampliada por la óptica del ocular.

Los microscopios tienen la capacidad de enfocar o hacer nítido el objeto moviendo el objeto o la lente.
Aquí simplemente movemos el portaobjetivos con la mano. Ajustamos las distancias entre los componentes para ver una
imagen nítida.

# „Óptica finita“ frente a „Óptica infinita“

VV = 250 mmmm; aumento del ocular; aumento general; sorprenderá.; Eyepiece; fOkular; Objective; Objektiv; fObjektiv; Object; Objekt; Tube lens; fTubuslinse; Intermediate Image

¿Cuál es el aumento de la imagen intermedia? ¿Y cuál es el aumento después del ocular?

aumento del objetivo

como está escrito en él

La imagen es mayor que con el
microscopio infinito. El aumento
del objetivo es de 4x. Si ha
calculado el aumento con el mi-
croscopio anterior, esto no le

La imagen intermedia ahora sólo
está formada por el objetivo y se
encuentra a 160 mm por detrás
de él. Descubriremos por qué en
el siguiente paso.

defined tube length of the finite objective

Das Objektiv ist auch eine Sammellinse mit kurze Brennweite.

4/0.10
160/0.17

2 x convergentes

Mira a través del objetivo simple de 50 mm y luego a través del objetivo doble a la rejilla.

Mira a través del objetivo de 50 mm y luego mira a través del objetivo el texto pequeño.

¿Cuál de las lentes aumenta más? ¿Qué hay
escrito ahí? | ¿Cómo cambian el aumento y el campo de visión?

# Objetivo y ocular

Abra los cubos con los objetivos de 50 mm. Coloca ahora los dos objetivos de 50 mm en un cubo de forma que las „barrigas“ de los lentes apunten la una hacia la otra.

Mira la lente. ¿Qué hay dentro? ¿Qué hay escrito en ella?

4/0.10
160/0.17

# Esta es la lente objetiva

Un objetivo es un sistema óptico que proporciona una representación ampliada de un punto de partida. Los distintos valores indicados en el objeto tienen distintas implicaciones:

Corrección del cubreobjetos :
A veces se utiliza un cubreobjetos para sellar la muestra. La lente debe corregirse para este grosor (0,17mm).

Apertura numérica:
Determina la capacidad de captar la luz y, por tanto, la resolución óptica.

Longitud del tubo:
significa infinito,160 significa 160 mm y es la longitud de tubo más utilizada según la norma DIN

Aumento:
Los aumentos habituales
son 4x, 10x, 40x, 100x.

El objetivo 4x sólo tiene una lente. Los objetivos de mayor aumento son sistemas de lentes completos.

El objetivo también es convergente y tiene una distancia focal corta. El objetivo 4 x tiene una distancia focal de f =32 mm.
Cuando se utiliza como lupa, tiene un aumento mayor que el objetivo de 50 mm. El campo de visión es

# Este es el ocular

Un ocular es en realidad una lupa porque amplía la imagen intermedia. El ocular que utilizamos aquí es un ocular llamado
Ramsden.
También se puede utilizar una sola lente como ocular. Sin embargo, con el ocular Ramsden, que consiste en un sistema de len-
tes, el campo de visión es mejor porque produce menos errores en el borde del campo de visión. El ocular Ramsden consta de
dos lentes con la misma distancia focal. Su distancia focal

fRamsden-Okular= 3/4 fLinse

¿Cuál es el aumento del ocular Ramsden? =

La escala de la imagen es mayor a distancias cortas
del objeto que con un solo objetivo de 50 mm.

Cada ocular tiene un denominado disco de Ramsden,
que es el diámetro más pequeño del haz de luz que
sale del microscopio a través del ocular.

El campo de visión es mayor y la imagen parece más

nítida con el ocular Ramsden.

# Microscopio Smartphone

Mirror; Mikroskopobjektiv; Microscope Object; Ramsden-Eyepiece; Object; Illumination

Construye el microscopio del smartphone como se muestra. Utiliza
dos cubos cualesquiera para colocar el smartphone de forma segu-

or smartphone ca-
mera

Construye el mi-
croscopio como un
sándwich.
Añade una
segunda capa uti-
lizando una placa
base. Mira por el
ocular desde arriba.

Sustituya la pie-
za ocular Rams-
den por la lente
de 50 mm. ¿Qué
es mejor para la
vista y qué para
el smartphone?

# ¿Mejor con smartphone o a ojo?

La cámara del smartphone tiene un objetivo con una distancia focal muy corta porque tiene que caber en el delgado smart-
phone. El objetivo crea entonces una imagen en el sensor de la cámara cuyas propiedades son similares a las del ojo humano.
El ojo puede representar objetos tanto de lejos como de cerca. Esta propiedad se denomina acomodación.
La cámara del smartphone también puede hacerlo, pero se denomina enfoque automático. Describe la capacidad

de mover objetos a diferentes distancias de forma nítida en el sensor.

La imagen del ocular llega en rayos paralelos, como si procediera del infinito. Se observó con el ojo relajado (mirando

a lo lejos) o con una cámara enfocada al infinito.

# ¿Mejor con smartphone o a ojo?

espejos.

Para poder ver la imagen del microscopio, la pupila -es decir, la „abertura“ que limita la incidencia de la luz- debe coincidir con
el disco de Ramsden del ocular. La pupila del ojo está fija en su interior y no puede acercarse al ocular. En cambio, la pupila de
la cámara del smartphone está muy cerca de la superficie del móvil. Debido a esta diferencia, se necesita una distancia dife-
rente al ocular para el ojo y la cámara.

¿Cuál es el aumento de este microscopio?
Fórmula para calcular el aumento

Con el ocular Ramsden, el disco Ramsden está más
cerca del cubo y tiene un diámetro menor, lo que fun-
ciona bien para la cámara del smartphone.

pupila del ojo

El disco de Ramsden del objetivo simple de 50 mm
tiene un diámetro mayor, lo que resulta más cómodo
para observar la muestra con el ojo. A través del ocular
parece como si la imagen estuviera en el espejo situa-
do debajo. Las lentes de 50 mm tienen un diámetro
grande, por lo que al utilizar una sola lente como ocular,
el campo de visión está limitado por el tamaño de los

pupila de la cámara

Lupe; Projektor; Galilei-Fernrohr; Kepler-Fernrohr; „Unendlich“-Mikroskop; „Unendlich“-Mikroskop mit Okular; „Endlich“-Mikroskop - Zwischenbild; Ramsden-Okular; Smartphone Mikroskop mit Ramsden-Okular; Resultados de los cálculos

## „Endlich“-Mikroskop - Gesamtvergrößerung

# Glossary

Lado del objeto
lado en relación con la lente en la que está localizado el elemento ;a la izquierda en los esquemas
Lado de la imagen
lado relativo a la lente en la que se forma la imagen real; La imagen virtual está en el mismo lado que el objeto. Rayo central
Los rayos centrales atraviesan la lente delgada sin cambios.
Rayos paralelos
Todos los rayos que discurren paralelos al eje óptico son refractados por la lente de tal forma que se encuentran en el punto focal. Como el punto más brillante se encuentra directamente detrás de la lente, esto sólo ocurre en las lentes convergentes.
Rayos focales
Todos los rayos que atraviesan un punto focal o salen de él son refractados por la lente de forma que pasan paralelos al eje óptico situado detrás de la lente.
Iluminación
En microscopía se necesita una fuente de iluminación para poder ver el objeto. Puede ser, por ejemplo, una linterna o el reflejo del sol.
Lupa (también cristal de aumento o cristal ardiente) El dispositivo óptico más simple que aumenta el objeto para el ojo humano.
Telescopio (también telescopio de lente o refractor) Instrumento óptico que, cuando se utiliza, hace que los objetos distantes parezcan varias veces más cercanos o más grandes.
Lente
Un sistema óptico que crea una imagen óptica real de un objeto
Ocular
La parte ocular de un sistema óptico
Microscopio óptico
Microscopio que utiliza la luz para obtener imágenes muy ampliadas de estructuras u objetos pequeños. Lente tubular
Un objetivo que crea una imagen intermedia real a partir de los rayos paralelos de luz tras el objetivo de óptica infinita
Imagen intermedia
Imagen de aumento del objeto producida por la lente Espejo
Una superficie reflectante lo suficientemente lisa como para que la luz reflejada en ella cree una imagen.

Object page
side in relation to the lens on which the object (item) is located; left in the schemes
Image side
side relative to the lens on which the real image is formed; The virtual image is on the same side as the object. Center ray
Center rays pass through the thin lens unchanged. Parallel rays
All rays that run parallel to the optical axis are refracted by the lens in such a way that they meet at the focal point. As the brightest point directly behind the lens, this is only found in converging lenses.
Focal rays
All rays that pass through a focal point or come out of the focal point are refracted by the lens in such a way that they pass parallel to the optical axis behind the lens. Illumination
In microscopy, you need an illumination source to be able to see the object. This can e.g. B. a flashlight or the reflection from the sun.
Magnifying glass (also magnifying glass or burning glass) The simplest optical device that magnifies the object for the human eye
Telescope (also lens telescope or refractor)
An optical instrument that, when used, makes distant objects appear many times closer or larger

Lens
An optical system that creates a real optical image of an object
Eyepiece
The eye-side part of an optical system
Light microscope
A microscope that uses light to produce highly magnified images of small structures or objects
Tube lens
A lens that creates a real intermediate image from the parallel rays of light after the infinity optics lens
Intermediate image
Magnifying image of the object produced by the lens Mirror
A reflective surface smooth enough for light reflected off it to create an image
Accommodation of the eye
A dynamic adjustment of the refractive power of the eye; It means that objects at different distances can be imaged sharply on the retina.
Autofocus
Unlike accommodation, in most cases of autofocus, the focal length remains constant and the distance between the lens and the screen is varied.

# Impressum

Productdesign: Barbora Maršíková, Benedict Diederich

Layout: Katrin Uhlig, Benedict Diederich www.openUC2.com

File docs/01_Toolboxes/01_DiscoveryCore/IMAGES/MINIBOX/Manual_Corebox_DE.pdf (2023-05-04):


# CoreBOX

Sammellinse; Probenhalter; Spiegel; Spiegel Zerstreuungslinse; Inhalt der CoreBOX; Probenhalter und Linearstage Hält das Objekt und bewegt das Objektiv; Spiegel, Linse, Okular und Objektiv Fokussiert und Reflektiert; Reinigung der Linsen Nutze ein Brillenputztuch; Vorsicht! Berühre nicht das Glas!; Linear Stage; Mikroskopobjektiv; Okular; Taschenlampe

Würfel

Würfel (Hälfte)

Einsatz (z.B. Probenhalter)

Würfel (Hälfte)

Grundplatte

Grundplatte mit Magneten

# You.See.Too.? UC2!

Das Kernelement des UC2-Projekts ist ein einfacher Würfel. Der Würfel besteht aus zwei Hälften und beherbergt einen verschiebbaren Einsatz. Der Einsatz kann verschiedene optische Komponenten (z.B. Linsen, Spiegel) halten, womit sich mit jedem Würfel unteschiedliche Funktionen realisieren lassen. Die Würfel, sowie die in alle Richtungen erweiterbaren Grundplatten im Puzzleformat sind Spritzgegossen und haben dadurch eine hohe Präzision. Gehalten werden die Teile per Formschluss, was die Nutzung von Magneten und Schrauben erübrigt. Die Einsätze im Stopschildformat lassen sich schnell an neue Komponenten anpassen und finden im Würfel platz.

# Würfeltyp 1

Spritzguss mit Steckverbindung

Der Würfel lässt sich auf eine Grundplatte montieren. Die Grundplattenmodule lassen sich wie Puzzle zusammenstecken.

# UC2 zum Selberdrucken

Neben dem spritzgussfähigen Design kommt der Würfel auch in einer druckbaren Version daher. Beide Würfel sind miteinander kompatibel, jedoch lässt sich der Würfel bestehend aus Deckel und Korpus besser drucken. Die magnetischen Schrauben dienen dazu, sich mit den Kugelmagneten auf der Platte zu verbinden. Durch die Kombination verschiedener Würfelmodule lassen sich ganz einfach verschiedene optische Aufbauten zusammenbauen. Mit jedem Würfel kann eine neue Funktion hinzugefügt werden. Deiner Kreativität sind keine Grenzen gesetzt.

# Würfeltyp 2

3D gedruckt mit Magnetverbindung

Grundplatte

Grundplatte

Würfel

Würfel (Körper)

Schrauben (magnetisch)

Kugelmagnete

Würfel (Deckel)

In der 3D-gedruckten Grundplatte sind kleine Kugelmagnete eingelassen, auf die die Würfel gesteckt
werden.
Willst du mehr Würfel haben? Dann kannst du
sie selbst bauen. Du findest alles hier.

So passen die Würfel zusammen; cken und nicht verkippt sind.; Bild zeigt dir, wie das geht.; Das kann eine Linse; durch an. Halte den; Wie sieht das Bild aus?

Achte darauf, dass die Würfel richtig auf der Platte ste-

Tipp: Am besten halten die Würfel im „Sandwich“-Format, wobei die Platten die Würfel oben und unten halten

Wenn du kein scharfes Bild siehst, verschiebe die Einsätze (z.B. Linse) so lange, bis du es klar siehst. Der grüne Pfeil im

Nimm einen oder mehrere der Würfel, in denen eine Linse steckt und schaue dir das hier abgebildete UC2 Symbol da hin-

Würfel dabei in der Hand und verändere den Abstand zwischen der Linse und dem Bild.

Verschiedene Linsen haben unterschiedliche Fähigkeiten. Welchen Unterschied beobachtest du zwischen den

Mit der Zerstreuungslinse (f = −50mm) ist das Bild immer verkleinert und immer aufrecht.

Haben die Antworten noch mehr Fragen aufgeworfen? Dann fahre fort, um herauszufinden, wie genau die Linsen funktionieren…

Wir gehen davon aus, dass unsere Linsen so genannte „dünne Linsen“ sind. Das bedeutet, dass wir sie als eine Ebene betrachten können und uns nicht um ihre Dicke kümmern. Das macht Erklärungen und Berechnungen viel einfacher.

Die Zerstreuungslinse (Streulinse) heißt manchmal auch negative oder konkave Linse. Der mittlere Teil der Linse ist immer dünner als der Rand.

Mit der Sammellinse kann das Bild vergrößert werden. Die Vergrößerung ist für die 50-mm-Linse und die 100-mm-Linse unterschiedlich. Das Bild kann aufrecht oder umgekehrt sein.

Die Sammellinse heißt auch positive oder konvexe Linse. Der mittlere Teil der Linse ist immer dicker als der Rand.

# Linsen

In der Strahlenoptik wird das Licht als Strahlenbündel (Pfeile) dargestellt, was eine Vereinfachung der physikalischen Eigenschaften von Licht mit sich bringt. Ein Strahl hat eine Richtung und wird daher mit einem Pfeil gezeichnet. Eine Linse „bricht“ den Strahl und ändert so seine Richtung.

Sammellinsen brechen die
Lichtstrahlen, die parallel zur optischen Achse laufen, in einem Punkt, der Brennpunkt gennant wird.

Zerstreuungslinsen brechen die Lichtstrahlen, die parallel zur optischen Achse laufen als würden sie einem Punkt entspringen, der „virtueller“ Brennpunkt gennant

Die Brennweite einer Linse entspricht hier der Distanz von der Linse zur Brennebene, auf der der Brennpunkt liegt. Sie wird in Millimeter angegeben (f = mm).

# Linsen „brechen“ die Lichtstrahlen

Die Brennweite der Linse findest du als eine gedruckte Nummer auf den Linsenhaltern. Die CoreBOX enthält eine 100-mm-Sammellinse, zwei 50-mm-Sammellinsen und eine -50-mm-Zerstreuungslinse. Die Zahlen geben die Brennweite an.

Sammellinsen

In der „echten“ Welt Auf dem Papier

Fokus – Brennpunkt F‘ Sammellinse

Brennebene

Brennweite f (positiv)

Parallelstrahlen

optische Achse

Parallelstrahlen

„Brennpunkt“ F‘

Brennebe-

Brennweite f (ne-

Zerstreuungs-

optische

Zerstreuungslin-

In der „echten“ Welt Auf dem Papier

# Linsen-Abbildung

Nimm jetzt die Linsen-Würfel zur Hand. Versuche, mit der passenden Linse die jeweilige Angabe über die Brennweite in den abgebildeten Würfeln zu entziffern. Bewege die Linse über der Schrift bis sie die gleiche Größe hat wie der Text „UC2“ in der Mitte.

UC2

Was passiert, wenn du eine Linse mit der falschen Brennweite verwendest?

Kannst du den Text in der gleichen Größe und Ausrichtung wie das „UC2“ sehen? Was passiert, wenn du den Abstand zwischen der Linse und dem Bild veränderst?

# Abbildung eines Gegenstandes durch eine positive Linse

Als Beispiel nehmen wir die Sammellinse. Wir starten mit einem Gegenstand (grüner Pfeil) und schauen, was mit den Strahlen passiert, die von der Spitze aus starten. Es gibt unendlich viele Strahlen in alle Richtung, für das Zeichnen der Abbildung reichen uns aber die drei folgenden Strahlen:
1. Der Mittelpunktstrahl (orange) geht ungestört durch das Zentrum der Linse.
2. Der Brennpunktstrahl (gelb) startet auch von der Spitze des Pfeils, geht aber durch den objektseitigen Brennpunkt in der Brennweite f. Nach der Linse verläuft er auf gleicher Höhe weiter, aber nun parallel zur optischen Achse.
3. Der Parallelstrahl (rot) läuft zunächst parallel zur optischen Achse, wird dann aber an der Linse so gebrochen, dass er durch den bildseitigen Brennpunkt in der Brennweite f verläuft.
Das Bild entsteht dort, wo sich alle Strahlen schneiden. Das Prinzip ist für alle Punkte bzw. die davon ausgehenden Strahlen eines Objekts gleich. Je nach dem, welche Linse benutzt wird und je nach Position des Objekts, verändern sich die Eigenschaften des Bildes, die Größe, die Orientierung und die Position.
Brennweite | Brennweite

Parallelstrahl

Brennebene | Brennebene

optische Achse

Brennpunktlstrahl

Bild

Linse

Mittelpunktstrahl

Gegenstand

f = +100mm

# f = -50mm

Bild

# Abbildung eines Gegenstandes durch eine negative Linse

Im Fall der Zerstreuungslinse benutzen wir die gleiche Methode, um den Strahlengang abzubilden. Anders als im Fall der Sammellinse ist das Bild immer verkleinert und virtuell. Die Vergrößerung ist von der Position des Gegenstands vor der Linse abhängig. Anders als bei der Sammellinse entsteht das Bild auf der Objektseite und heißt damit virtuelles Bild. Du kannst es direkt mit deinen Augen sehen aber nicht auf einen Bildschirm projizieren.

Die Art und Weise, wie eine Linse ein Bild erzeugt, ist vorhersehbar, wenn man die Brennweite dieser Linse kennt. Deshalb muss ein bestimmter Abstand eingehalten werden, damit du die Schrift mit der angegebenen Linse auf dem vorhergehenden Blatt erkennst.

Die Vergrößerung und der Ort, an dem das Bild entsteht, hängen von der Brennweite der Linse und vom Abstand zwischen Linse und Objekt ab.

Mit der Zerstreuungslinse (f = -50mm) siehst du immer ein verkleinertes virtuelles Bild. Ein virtuelles Bild kann nur mit dem Auge betrachtet werden. Bislang haben wir nur virtuelle Bilder gesehen.

Die Sammellinse als Lupe; Die Lupe

Nimm den UC2 Linsen-Würfel mit der Brennweite f = 50mm und benutze ihn als eine Lupe.

Brennebene | Brennebene

Gegenstand

Gegenstand- | Bild-
2xf | 2xf

… ist eine einfache Sammellinse mit kleiner Brennweite.

Leg‘ den Linsen-Würfel auf das Blatt und verschiebe die Linse in eine Höhe, bis du den hier geschriebenen Text lesen kannst.

Die Lupe ist das einfachste optische Gerät!

Kannst du durch die Sammellinse die kleinen Buchstaben lesen? Was steht dort geschrieben?

f

t

Das machen Sammellinsen; Linse entspricht, dann ist das Bild … • umgekehrt • seitenvertauscht • verkleinert • reell; entspricht, dann ist das Bild … • umgekehrt • seitenvertauscht • gleich groß • reell; dann ist das Bild … • umgekehrt • seitenvertauscht • vergrößert • reell; Bild; Objekt; Gegenstand-; Bild-; Bildweite (b) Der Abstand zwischen der Linsenebene und dem von der Linse erzeugten Bild wird als b bezeichnet.; Gegenstandsweite (g) Der Abstand zwischen dem Objekt und der Lin- senebene wird als g be- zeichnet.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

Von den Sammellinsen hängt die Vergrößerung und Position des Gegenstands ab.

Wenn der Abstand zwischen Objekt und Linse mehr als dem doppelten der Brennweite der

Wenn der Abstand zwischen Objekt und Linse genau der doppelten Brennweite der Linse

Wenn der Abstand zwischen Objekt und Linse mehr als die Brennweite und weniger als dem doppelten der Brennweite der Linse entspricht,

# Darum vergrößert die Lupe

Lupeneffekt
Wenn der Abstand zwischen Objekt und Linse weniger als der Brennweite der Linse entspricht, dann ist das Bild …
- aufrecht
- seitenrichtig
- vergrößert
- virtuell

Berechne die Vergrößerung der Lupe mit der folgenden Formel:
Die Lupe ist das einfachste aller optischen Geräte, denn es besteht bloß aus einer einfachen Sammellinse mit passender Brennweite. Warum vergrößert der Würfel mit der 50mm den kleinen Text? Befindet sich das Objekt vor der Brennweite der Linse – also weniger als 50mm vor der Linse – erzeugt die Linse ein virtuelles Bild, welches hinter dem eigentlichen Objekt liegt. Das Auge nimmt es vergrößert wahr. Schau dir dazu das Diagramm oben an.

250mm ist die Entfernung der deutlichen Sehweite – also der Abstand zwischen Objekt und Auge bei dem die meisten Menschen gut lesen können. Mehr dazu später in der „Akkommodation“ des Auges.

Gegenstandseite | Bildseite
2xf | f | f | 2xf

# V = 250 mm

f

# So funktioniert ein Kinoprojektor

Nimm dir den UC2-Linsenwürfel mit der Brennweite f = 50mm und platziere ihn hinter den Probenhalterwürfel. Der Abstand zwischen dem Objekt und der Linse (also die Gegenstandsweite g) sollte ca. 60mm entsprechen. Wenn du nun mit der Taschenlampe das Objekt beleuchtest, wirst du es in einem Abstand von ca. 300mm auf der Wand scharf sehen. Ein Kinoprojektor hat statt des Objekts einen Filmstreifen und natürlich eine viel stärkere Lichtquelle.

Wie ist das Bild orientiert? Schiebe die Linse in dem Würfel hin und her und beobachte, wann das Bild scharf ist. Finde das Bild für g = 60mm, 65mm, 70mm und messe den Abstand zwischen der Linse und dem Bild.

Benutze eine Taschenlampe (z.B. von deinem Handy) als Lichtquelle und halte es vor das Objekt.

# So funktioniert der Projektor

Wo ist das Bild?
Bei der Abbildung eines Gegenstands durch eine Sammellinse hängen Lage und Größe des Bildes von der Entfernung (g) des Gegenstands zur Linse und von deren Brennweite (f) ab.
Die Linsengleichung beschreibt den Zusammenhang zwischen der Bildweite (b) und Objektweite (g):

Wie groß ist das Bild?
Die Vergrößerung des Objekts auf dem Schirm lässt sich einfach mit der folgenden Formel ausrechnen:
2xf | f | 2xf

Brennweite
f
Entfernung des Gegen- | Entfernung des Bildes

Bildgröße B

Gegenstandsgrö-

Beleuchtung

Sammellinse 50mm

g

2xf

Objekt

g | b

f

1
ff = 1
gg

+

1
bb

# VV = bb

# gg = BB

GG

einstimmt.; verschiedenen Werte g und b.; Brennweite f; Gegenstandsgröße G; g Entfernung des Gegenstands; b Entefernung des Bildes; So funktioniert der Projektor; für g = 60mm b = 300mm für g = 65mm b = 217mm für g = 70mm b = 175mm; Bildgröße B

Prüfe, ob deine Beobachtung mit der Berechnung über-

Berechne die Vergrößerung des Projektors für die

Das ist ein Galilei-Fernrohr; fObjektiv – fOkular; Wie sieht das Bild aus? Wie ist das Bild orientiert?; Bild zu sehen!; Zerstreuungslinse -50mm; Okular; Sammellinse 100mm; Objektiv

Stell die Linsen-Würfel auf das Blatt, wie in dem Diagramm gezeigt und schaue dann durch das Fernrohr in die Ferne.

Unsere Linse hat eine Brennweite von f = 50 mm.

Der Projektor erzeugt immer ein vergrößertes, invertiertes (umgekehrtes) Bild. Die Position des Bildes und seine Vergrößerung hängen von der Position und der Größe des Objekts ab.

Während du durch das Fernrohr schaust, passe die Abstände zwischen den Komponenten an, um ein scharfes

So funktioniert das Galilei-Fernrohr; Sammellinse; Zerstreuungslinse; lange Brennweite; kurze Brennweite; Parallelstrahlen; Die Linse, die dem Auge zugewandt ist, nennt man Okular.; Die Linse auf der Ob- jektseite nennt man Objektiv.; Objektiv; Okular; fObjektiv; fOkular

Ein Fernrohr ist ein optisches Instrument, das entfernte Objekte um ein Vielfaches näher oder größer erscheinen lässt.

So funktioniert das Galilei-Fernrohr; Formel zur Berechnung der Vergrößerung; Okular; fOkular; Objektiv; fObjektiv; den können.; Das Bild ist immer; • aufrecht • seitenrichtig Das Sichtfeld ist klein.

Wie lautet die Vergrößerung dieses Galilei-Fernrohrs?

Sichtfeld bezeichnet den Bereich im Bildwinkel einer optischen Einrichtung, innerhalb dessen Objekte aufgezeichnet wer-

Das Galilei-Fernrohr wird auch in Operngläsern verwendet.

- vergrößert mit der Vergrößerung aus obiger Formel Mit diesem Fernrohr kann man keine sehr hohe Vergrößerung erreichen. Dafür ist es sehr kompakt.

# Das ist ein Kepler-Fernrohr

# So funktioniert das Kepler-Fernrohr

fObjektiv + fOkular; Objek-; Okular; Sammellinse; lange Brennweite; kurze Brennweite; Objektiv; fObjektiv; fOkular; leer; Sammellinse 100mm

Stell die Linsen in die richtige Position, wie in dem Diagramm gezeigt. Dann schaue durch das Fernrohr in die Ferne.

Während du durch das Fernrohr schaust, passe die Ab-
stände zwischen den Komponenten an, um ein scharfes

Wie sieht das Bild aus?
Wie ist das Bild orientiert?

Bild zu sehen!

Diese Art von Fernrohr wird häufig in der Astronomie benutzt.

# Das ist ein Beobachtungsfernrohr

Das Beobachtungsfernrohr ist lang, deshalb ist das Schema hier nicht so groß wie in der Realität. Stell‘ die Linsen in die richtige Position wie hier dargestellt und schaue durch das Fernrohr in die Ferne.

Wie sieht das Bild hier im Vergleich zum Kepler-Fernrohr aus?

Während du durch das Fernrohr schaust, passe die Abstände zwischen den Komponenten an, um ein scharfes Bild zu sehen!

So funktioniert das Kepler-Fernrohr; Formel zur Berechnung der Vergrößerung; Das Bild ist immer; • umgekehrt • seitenvertauscht; aber kein Problem.; Objektiv; Okular; fObjektiv; fOkular

Was ist die Vergrößerung dieses Kepler-Fernrohrs?

- vergrößert mit der Vergrößerung aus obigerFormel

Das Sichtfeld ist größer als beim Galilei-Fernrohr.

Dieses Teleskop kann eine höhere Vergrößerung als das Galilei-Fernrohr erreichen. Es erzeugt aber ein umgekehrtes Bild. Für die Beobachtung der Sterne ist das

fObjektiv + 2xfUmkehrlinse | 2xfUmkehrlinse + fOkular

Umkehrlinse

Sammellinse 100mm | Sammellinse 50mm
Objektiv | Okular
leer | leer | leer | leer | leer

Sammellinse

Kepler-Fernrohr; Okular; fOkular; 2xfUmkehrlinse; Sammellinse; Objektiv; Umkehrlinse; fObjektiv
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

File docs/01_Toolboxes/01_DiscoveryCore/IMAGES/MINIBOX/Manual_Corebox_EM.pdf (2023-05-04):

# CoreBOX

# What‘s inside?

Specimen holder and linear stage:
Holds the specimen and moves the objec-
tive
Mirror, lens, eyepiece and objective:
Focuses and reflects

Please do not touch the glass!
Cleaning the lenses:
Use a lens cleaning cloth

Cube

Cube (Half)

Insert (e.g. Sample Holder)

Cube (Half)

Baseplate

# You.See.Too.? UC2!

The core element of the UC2 project is a simple cube. The cube consists of two halves and houses a sliding insert. The insert can hold different optical components (e.g. lenses, mirrors), which means that different functions can be realised with each cube. The cubes, as well as the base plates in puzzle format, which can be extended in all directions, are injection moulded and therefore have a high precision. The parts are held in place by a positive fit, which eliminates the need for magnets and screws. The inserts in stop plate format can be
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

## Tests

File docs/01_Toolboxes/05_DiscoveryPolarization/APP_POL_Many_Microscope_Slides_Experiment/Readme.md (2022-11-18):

# Many Microscope Slides Experiment

<p align="center">

</p>

There are different ways of producing polarized light from unpolarized light.  In an example process: light travels from medium 1 to medium 2. Some part of the incident light reflects from the surface of medium 2. This reflected light can be partially polarized light or totally polarized light in the Brewster angle. Another part of the initial light is refracted to medium 2 as a partially polarized light. You can have more detailed information about the polarization of the light by reflection  [in the Brewster Angle Experiment](../../APPLICATIONS/APP_POL_Brewster_Angle_Experiment).

However, transmission light eventually polarizes based on the polarization by reflection, when the light is transmitted many times through several microscope slides.

In the experiment, a medium is constructed with 7 adjacent microscope slides by the experimenter. Then, unpolarized light rays travel through microscope slides. After this glass medium, many times transmitted rays will be polarized. If we transmit light through only one microscope slide, refracted light will be partially polarized. But if we repeat this process many times such as 7 or more times, in one point transmitted light will be perfectly polarized.

<p align="center">

</p>

*Polarization by Refraction:* Unpolarized or partially polarized incoming light travels, reflects as partially s polarized and transmits as partially p polarized between medium 1and medium s2.

## Parts

### Modules for this setup

|  Name | Properties  |  Price | Link  | # |
|---|---|---|---|---|
|  4×1 Baseplate | Skeleton of the System | 5.47 €  | [Base-plate](../../CAD/ASSEMBLY_Baseplate)  | 1 |
|  MODULE:  *Polarizer Cube* | It holds the linearly polarizing filter  |  4.31 €  | [Linear Polarizer](../../CAD/ASSEMBLY_POL_Linear_Polarizer)  | 1 |
|  MODULE: *Many Microscope Slides Holder* | It hold 7 or more microscope slides back to back  | 2.11 €  | [Slides Holder](../../CAD/ASSEMBLY_CUBE_Sample_Holder)  | 1 |
|  MODULE: *Laser Cube* | LASER source holder  | 17.68 €  | [Light Source ](../../CAD/ASSEMBLY_CUBE_Laser)  | 1 |
|  EXTRA MODULE: Screen Holder Cube | It holds the Display Screen (Not Used in Practice) | 1 €  | [Screen](../../CAD/ASSEMBLY_CUBE_Sample_Holder)  | 1 |

### Parts to print

* 1 × [Base-plate 4×4](/POLARISATION/SLIDES/Assembly_Cube_Baseplate_4x1_v2.stl)
* 2 × [Cube base 1×1](/POLARISATION/SLIDES/10_Cube_1x1_v2.stl)
* 3 x [Cube lid 1×1](/POLARISATION/SLIDES/10_Lid_1x1_v2.stl)
* 1 × [Polarizer Guide](/POLARISATION/SLIDES/20_POL_Cube_Insert_Linear_Polarizer_Guide.stl)
* 1 × [Polarizer Wheel](/POLARISATION/SLIDES/20_POL_Cube_Insert_Linear_Polarizer_Wheel.stl)
* 1 × [Polarizer Lid](/POLARISATION/SLIDES/20_POL_Cube_Insert_Linear_Polarizer_Lid.stl)
* 1 x [Many Microscope Slides Holder](/POLARISATION/SLIDES/20_Cube_Sampleholder.stl)
* 2 × [Laser Mount](/POLARISATION/SLIDES/20_Cube_Insert_Laser_Holder_v2.stl)
* 1 x [Laser Clamp](/POLARISATION/SLIDES/00_Laser_Clamp_OnOffSwitch.stl)   

<p align="center">

</p>  

##  Additional components
* Check out the [RESOURCES](../../TUTORIALS/RESOURCES) for more information!
* 1 × Linear Polarizing Sheet [🢂](https://amazon.de/-/en/Polarizing-A4-Sheet-Polarizer-Educational-Polarized/dp/B06XWXRB75/ref=pd_sbs_421_3/262-2115536-7173904?_encoding=UTF8&pd_rd_i=B06XWXRB75&pd_rd_r=b88e7340-b061-4e0b-8daa-8ec533fd7c71&pd_rd_w=qlkAY&pd_rd_wg=At9EZ&pf_rd_p=a03ac387-6e4d-4f6b-96b6-1853da0bb37b&pf_rd_r=49HX2Z4Q5KRZSQ2FWRQR&psc=1&refRID=49HX2Z4Q5KRZSQ2FWRQR)
* 16 × 5 mm Ball magnets [🢂](https://www.magnetmax.de/Neodym-Kugelmagnete/Magnetkugel-Kugelmagnet-O-5-0-mm-Neodym-vernickelt-N40-haelt-400-g::158.html)
* 24 x Screws DIN912 ISO 4762 - M3×12 mm [🢂](https://eshop.wuerth.de/Zylinderschraube-mit-Innensechskant-SHR-ZYL-ISO4762-88-IS25-A2K-M3X12/00843%20%2012.sku/de/DE/EUR/)
* 3 x Screws DIN912 ISO 4762 M2×16 mm [🢂](https://www.amazon.de/Edelstahl-Sechskopf-Knopf-Schrauben-Unterlegscheiben-Sortiment-Aufbewahrung/dp/B073SS7D8J/ref=sr_1_fkmr0_1?__mk_de_DE=%C3%85M%C3%85%C5%BD%C3%95%C3%91&keywords=zylinderkopfschrauben+set+galvanisiert&qid=1565007371&s=diy&sr=1-1-fkmr0)
* 9 x Microscope Rectangular Coverslips [🢂](https://www.ebay.de/itm/223260964391?hash=item33fb63f627:g:pukAAOSwsGpb%7E14N)
* 1 × 5 mW Blue UV Laser Pointer [🢂](https://www.laserlands.net/5mw-450nm-blue-laser-pointer-pen.html)

<p align="center">

</p>  

##  Assembly

* [Baseplate](../../CAD/ASSEMBLY_Baseplate)
* [Linear Polarizer Cube](../../CAD/ASSEMBLY_POL_Linear_Polarizer)  
* [Microscope Slides Holders](../../CAD/ASSEMBLY_CUBE_Sample_Holder)   
* [LASER Holder Cube](../../CAD/ASSEMBLY_CUBE_Laser)    
__*EXTRA MODULES:*__
* [Sample Holder for Screen](../../CAD/ASSEMBLY_CUBE_Sample_Holder)

<p align="center">

</p>  

##  Results

We printed and assembled Many Microscope Slides Experiment modules parts. Then, we bought the necessary components and inserted them into the cubes.         
The printed and assembled Sample Holder Comb module with nine microscope glasses:

<p align="center">

</p>

You will find the basic version of the experiment without a Screen adn Linear Polarizer module below.

<p align="center">

</p>

Images of the resulting experimental setup;     
side view (top) , top view (bottom)

<p align="center">

</p>

<p align="center">

</p>

We can observe the direct effect of the rotational angle of the linear polarizer in the video below. Laser light travels to microscope slides and air gap media several times and gets close to fully polarized light.  We can see this effect eith adding Linear Polarizer cube.       
The intensity of passing light through linear polarizer  changes when the direction angle of the polarization filter changes 360 degrees.     

We can see the change with two videos below. They demonstrates the experiment from two different views.

<p align="center">

</p>

<p align="center">

</p>

## New Ideas

Rat-Tat! We are here to hear new ideas. Please don't shy and have a heart-to-heart talk with us.  :gift_heart:

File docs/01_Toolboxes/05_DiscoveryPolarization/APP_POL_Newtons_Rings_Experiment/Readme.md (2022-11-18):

# Newton's Rings Experiment

<p align="center">

</p>

Soap bubbles, oil slicks, or oxidized metal surfaces can create interference patterns under the white light illumination. In Newton's fringes, light reflects as a constructively or destructively interfered when the light waves travel through two surfaces. These combinations can be created using glass-air or air-glass contacts. These two interferences generate a concentric ring pattern of rainbow colours in white light illumination. In the same way, monochromatic light creates dark-light rings.    

The simplest example can be made using two well-cleaned microscope slides as interfaces. Air film is enclosed between two slides inconsistently, and irregular-coloured fringes are generated under the daily light. When the pressure on the microscope slides changes, fringes move and change.

In the Newton's Rings Experiment, we used a convex lens whose surface is placed on an optical plane glass, a microscope glass, from its long focal length side. These two pieces are held together with non-uniform thin air film. After light illumination through these surfaces,the air gap and random pressures on the microscope slide and plano-convex lens cause the generation of irregular coloured or single-colour fringes; Newton's Rings.

#### The details of Experiment Modules

Linear Polarizer is used in this experiment to visualize the polarization change of reflected lights from two media on the interference pattern.

Additional module design was made for combining the microscope glass slide and plano-convex lens inside one cube insert. You can see rendered image of the Newton's Rings Lens-Slide Holder Module from Inventor.  

<p align="center">
s
</p>

We used laser as a light souce in the setup. During the experiment, we extended beam size of the pen laser from 2 mm to 6 mm using a regular [Beam Expander Module](../../CAD/ASSEMBLY_CUBE_Beamexpander).

## Parts

### Modules for this setup

|  Name | Properties  |  Price | Link  | # |
|---|---|---|---|---|
|  4×4 Baseplate | Skeleton of the System |  21.79 €  | [Base-plate](../../CAD/ASSEMBLY_Baseplate)  | 1 |
|  MODULE: *Beam Expander Cube* | It expands the laser beam size  |  13.55 €  | [Beam Expander](../../CAD/ASSEMBLY_CUBE_Beamexpander)  | 1 |
|  MODULE: *Beam Splitter Cube* | It splits the incoming beam and recombine them  |  29.17 €  | [Beam Splitter Holder](../../CAD/ASSEMBLY_CUBE_Beamsplitter)  | 1 |
|  MODULE: *Newton's Rings Slide-Lens Holder Cube* | It creates Newton's Rings  | 7.54 €  | [Lens - Slide Holder](../../CAD/ASSEMBLY_POL_Newtons_Rings_Module )  | 1 |
|  MODULE:  *Polarizer Cube* | It holds the linearly polarizing filter  |  4.31 €  | [Linear Polarizer](../../CAD/ASSEMBLY_POL_Linear_Polarizer)  | 1 |
|  MODULE: *Laser Cube* | LASER source holder  | 17.68 €  | [Light Source](../../CAD/ASSEMBLY_CUBE_Laser)  | 1 |
|  EXTRA MODULE: Screen Holder Cube | It holds the Display Screen (Not Used in Practice) | 1 €  | [Screen](../../CAD/ASSEMBLY_CUBE_Sample_Holder)  | 1 |

### Parts to print

* 1 × [Base-plate 4×4](/POLARISATION/NEWTON/Assembly_Cube_Baseplate_4x4_v2.stl)
* 5 × [Cube base 1×1](/POLARISATION/NEWTON/10_Cube_1x1_v2.stl)
* 6 x [Cube lid 1×1](/POLARISATION/NEWTON/10_Lid_1x1_v2.stl)
* 1 x [Beam Expander Holder](/POLARISATION/NEWTON/20_Cube_Insert_Beamexpander_astromedia_v3.stl)
* 1 × [Beam Splitter Cube Holder](/POLARISATION/NEWTON/20_Cube_Insert_Beamsplitter.stl)
* 1 × [Newton's Rings - Lens & Slide Holder](/POLARISATION/NEWTON/20_POL_Cube_Insert_Newtons_Rings_LensHolder.stl)
* 1 × [Newton's Rings - Lens & Slide Holder Clamp](/POLARISATION/NEWTON/20_POL_Cube_Insert_Newtons_Rings_Lens_Clamp.stl)
* 2 × [Laser Holder](/POLARISATION/NEWTON/20_Cube_Insert_Laser_Holder_v2.stl)
* 1 x [Laser Clamp](/POLARISATION/NEWTON/00_Laser_Clamp_OnOffSwitch.stl)
* 1 × [Polarizer Guide](/POLARISATION/NEWTON/20_POL_Cube_Insert_Linear_Polarizer_Guide.stl)
* 1 × [Polarizer Wheel](/POLARISATION/NEWTON/20_POL_Cube_Insert_Linear_Polarizer_Wheel.stl)
* 1 × [Polarizer Lid](/POLARISATION/NEWTON/20_POL_Cube_Insert_Linear_Polarizer_Lid.stl)        
__*Extra Holder Parts but NOT USED in our experiment:*__
* 1 x [Sample Holder - comb](/POLARISATION/NEWTON/20_Cube_Sampleholder.stl)

<p align="center">

</p>  

##  Additional components
* Check out the [RESOURCES](../../TUTORIALS/RESOURCES) for more information!
* 1 × Linear Polarizing Sheet [🢂](https://amazon.de/-/en/Polarizing-A4-Sheet-Polarizer-Educational-Polarized/dp/B06XWXRB75/ref=pd_sbs_421_3/262-2115536-7173904?_encoding=UTF8&pd_rd_i=B06XWXRB75&pd_rd_r=b88e7340-b061-4e0b-8daa-8ec533fd7c71&pd_rd_w=qlkAY&pd_rd_wg=At9EZ&pf_rd_p=a03ac387-6e4d-4f6b-96b6-1853da0bb37b&pf_rd_r=49HX2Z4Q5KRZSQ2FWRQR&psc=1&refRID=49HX2Z4Q5KRZSQ2FWRQR)
* 64 × 5 mm Ball magnets [🢂](https://www.magnetmax.de/Neodym-Kugelmagnete/Magnetkugel-Kugelmagnet-O-5-0-mm-Neodym-vernickelt-N40-haelt-400-g::158.html)
* 44 x Screws DIN912 ISO 4762 - M3×12 mm [🢂](https://eshop.wuerth.de/Zylinderschraube-mit-Innensechskant-SHR-ZYL-ISO4762-88-IS25-A2K-M3X12/00843%20%2012.sku/de/DE/EUR/)
* 3 x Screws DIN912 ISO 4762 M2×16 mm [🢂](https://www.amazon.de/Edelstahl-Sechskopf-Knopf-Schrauben-Unterlegscheiben-Sortiment-Aufbewahrung/dp/B073SS7D8J/ref=sr_1_fkmr0_1?__mk_de_DE=%C3%85M%C3%85%C5%BD%C3%95%C3%91&keywords=zylinderkopfschrauben+set+galvanisiert&qid=1565007371&s=diy&sr=1-1-fkmr0)
* 1 x Beamsplitter Cube (Art. 2137) [🢂](https://optikbaukasten.de/)
* 1 x Microscope Rectangular Coverslips [🢂](https://www.ebay.de/itm/223260964391?hash=item33fb63f627:g:pukAAOSwsGpb%7E14N)
* 1 x Plano-Convex Lens [🢂](https://www.comaroptics.com/components/lenses/simple-convex-lenses/plastic-lenses)
* 1 × 5 mW Blue UV Laser Pointer [🢂](https://www.laserlands.net/5mw-450nm-blue-laser-pointer-pen.html)
* 1 x iPhone 5 Lens f'=3mm (separated from an iPhone camera spare part) [🢂](https://www.amazon.de/BisLinks%C2%AE-Facing-Kamera-Ersatz-Repair/dp/B01M9K9RVN/ref=sr_1_10?__mk_de_DE=%C3%85M%C3%85%C5%BD%C3%95%C3%91&keywords=lg+g3+camera&qid=1565005739&s=gateway&sr=8-10)
* 1 x Achromat Lens f' = 26,5 mm [🢂](https://pgi-shop.de/achromat-2-lens-oe-15-mm-f-26.5-mm/)

<p align="center">

</p>  

##  Assembly

* [Baseplate](../../CAD/ASSEMBLY_Baseplate)
* [Beam Expander Cube](../../CAD/ASSEMBLY_CUBE_Beamexpander)
* [Beam Splitter Cube](../../CAD/ASSEMBLY_CUBE_Beamsplitter)
* [Newton's Rings Slide-Lens Holder Cube](../../CAD/ASSEMBLY_POL_Newtons_Rings_Module)
* [Linear Polarizer Cube](../../CAD/ASSEMBLY_POL_Linear_Polarizer)
* [LASER Holder Cube](../../CAD/ASSEMBLY_CUBE_Laser)   
__*EXTRA MODULES:*__
* [Sample Holder for Screen](../../CAD/ASSEMBLY_CUBE_Sample_Holder)

##  Results

We started with building of UC2 Modules: design, print, assemble and be ready for testing. You can see our Beam Expander Cube on the 4x1 Baseplate below.

<p align="center">

</p>

Lens - Slide Holder Module is the key element for the generation of Newton's Rings. Necessary Module parts are shown in the image below.

<p align="center">

</p>

Assembled and Ready-To-Use module should look like ...

<p align="center">

</p>

***The experimental procedure*** begins with
* installation the Laser and Beam Expander Modules on the 4x4 Baseplate.

<p align="center">

</p>

* After checking the expansion of the laser beam width, Beam Splitter Cube is added to the setup.

<p align="center">

</p>

* One of the divided incoming beams is directed to the Newton's Rings Lens & Microscope Holder cube, and light reflects from the convex lens-plate glass combination through the beam splitter cube, then on observation screen.

<p align="center">

</p>

<p align="center">

</p>

Demonstrating the experiment is much easier with a laser light source and results in visible fringes. The Newton's Fringes will vary in colour from inner to outer circles if a white light source is replaced with a laser source.

Let's zoom in Newton's Fringes with more experiment images!

<p align="center">

</p>

The effect of the polarization angle change of the Linear Polarizer Filter can be seen in the video.

<p align="center">

</p>

## New Ideas
We are open to new ideas. Please contribute to the project freely, this place is a free country which is built by codes and machines :robot:

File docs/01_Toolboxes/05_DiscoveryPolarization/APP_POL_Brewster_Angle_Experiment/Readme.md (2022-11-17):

# Brewster Angle Experiment

<p align="center">

</p>

There are several ways to produce polarized light. Optical processes reflection or refraction can be easily used to achieve that.  
When unpolarized light rays travel through a dielectric or insulating material, reflected and refracted light rays from the flat surface are mostly partially polarized.  
The amount of reflected light is specified by the optical properties of the reflecting surface, such as plastic sheets, glass, or highways.         
The incident angle of the incoming electromagnetic lightwave and refractive indices of media in which light travels through them have an essential role in the polarization degree of the reflected and refracted polarized light beams.

You can see the reflection and transmission of unpolarized light with most of the incident angle (𝜃) values below.

<p align="center">

</p>

###### What is the Brewster angle?

When the incident ray travels from a less dense medium (n1) to a higher dense medium (n2) with a critical angle (𝜃_B), the reflected ray is perfectly s-polarized in which the orientation of the electric field vectors are perpendicular to the plane of incidence. Otherwise, the refracted beam has a 90-degree polarization angle, partially p-polarized. This critical angle is called a Brewster angle or polarization angle and is represented by 𝜃_B in the scheme below.

<p align="center">

</p>

Brewster angle can be easily calculated using refractive indices of traveling media of light. In our experiment, we used air (n1 = 1) as the first medium in which light comes first and reflects in this part and microscope slide glass (n2 = 1.5) as the second medium, and the light transmits through. When we calculate the Brewster angle for our experiment, it equals approximately 57 degrees, and we can find the equation below.  

<p align="center">

</p>

<p align="center">

</p>

## Parts

### Modules for this setup

|  Name | Properties  |  Price | Link  | # |
|---|---|---|---|---|
|  4×4 Baseplate | Skeleton of the System |  21.79 €  | [Base-plate](../../CAD/ASSEMBLY_Baseplate)  | 1 |
|  MODULE:  *Polarizer Cube* | It holds the linearly polarizing filter  |  4.31 €  | [Linear Polarizer](../../CAD/ASSEMBLY_POL_Linear_Polarizer)  | 1 |
|  MODULE: *Kinematic Microscope Slide Holder* | It is used to insert the microscope slide with Brewster angle (53 degrees)  |  3.7 €  | [Microscope Slide Holder](../../CAD/ASSEMBLY_CUBE_Mirror_Kinematic_45)  | 1 |
|  MODULE: *Laser Cube* | LASER source holder  | 17.68 €  | [Light Source ](../../CAD/ASSEMBLY_CUBE_Laser)  | 1 |
|  EXTRA MODULE: Screen Holder Cube | It holds the Display Screen (Not Used in Practice) | 1 €  | [Screen](../../CAD/ASSEMBLY_CUBE_Sample_Holder)  | 1 |

### Parts to print

* 1 × [Base-plate 4×4](./STL/Assembly_Cube_Baseplate_4x4_v2.stl)
* 3 × [Cube base 1×1](./STL/10_Cube_1x1_v2.stl)
* 3 x [Cube lid 1×1](./STL/10_Lid_1x1_v2.stl)
* 1 × [Polarizer Guide](./STL/20_POL_Cube_Insert_Linear_Polarizer_Guide.stl)
* 1 × [Polarizer Wheel](./STL/20_POL_Cube_Insert_Linear_Polarizer_Wheel.stl)
* 1 × [Polarizer Lid](./STL/20_POL_Cube_Insert_Linear_Polarizer_Lid.stl)  
* 1 × [Kinematic Slide Holder - Base](./STL/20_POL_Cube_Insert_Brewster_Angle_Kinematic_Mount_Base_57_degrees.stl)
* 1 × [Kinematic Slide Holder - Plate](./STL/20_POL_Cube_Insert_Brewster_Angle_Kinematic_Mount_Plate_57_degrees.stl)
* 1 × [Kinematic Slide Holder - Clamp](./STL/20_POL_Cube_Insert_Brewster_Angle_Kinematic_Mount_Clamp_57_degrees.stl)
* 2 × [Laser Holder](./STL/20_Cube_Insert_Laser_Holder_v2.stl)
* 1 x [Laser Clamp](./STL/00_Laser_Clamp_OnOffSwitch.stl)         
__*Extra Holder Parts but NOT USED in our experiment:*__
* 1 x [Sample Holder - comb](./STL/20_Cube_Sampleholder.stl)

<p align="center">

</p>  

##  Additional components
* Check out the [RESOURCES](../../TUTORIALS/RESOURCES) for more information!
* 1 × Linear Polarizing Sheet [🢂](https:/amazon.de/-/en/Polarizing-A4-Sheet-Polarizer-Educational-Polarized/dp/B06XWXRB75/ref=pd_sbs_421_3/262-2115536-7173904?_encoding=UTF8&pd_rd_i=B06XWXRB75&pd_rd_r=b88e7340-b061-4e0b-8daa-8ec533fd7c71&pd_rd_w=qlkAY&pd_rd_wg=At9EZ&pf_rd_p=a03ac387-6e4d-4f6b-96b6-1853da0bb37b&pf_rd_r=49HX2Z4Q5KRZSQ2FWRQR&psc=1&refRID=49HX2Z4Q5KRZSQ2FWRQR)
* 67 × 5 mm Ball magnets [🢂](https:/www.magnetmax.de/Neodym-Kugelmagnete/Magnetkugel-Kugelmagnet-O-5-0-mm-Neodym-vernickelt-N40-haelt-400-g::158.html)
* 28 x Screws DIN912 ISO 4762 - M3×12 mm [🢂](https:/eshop.wuerth.de/Zylinderschraube-mit-Innensechskant-SHR-ZYL-ISO4762-88-IS25-A2K-M3X12/00843%20%2012.sku/de/DE/EUR/)
* 3 x Screws DIN912 ISO 4762 M2×16 mm [🢂](https:/www.amazon.de/Edelstahl-Sechskopf-Knopf-Schrauben-Unterlegscheiben-Sortiment-Aufbewahrung/dp/B073SS7D8J/ref=sr_1_fkmr0_1?__mk_de_DE=%C3%85M%C3%85%C5%BD%C3%95%C3%91&keywords=zylinderkopfschrauben+set+galvanisiert&qid=1565007371&s=diy&sr=1-1-fkmr0)
* Microscope Rectangular Coverslips [🢂](https:/www.ebay.de/itm/223260964391?hash=item33fb63f627:g:pukAAOSwsGpb%7E14N)
* 1 × 5 mW Blue UV Laser Pointer [🢂](https:/www.laserlands.net/5mw-450nm-blue-laser-pointer-pen.html)

<p align="center">

</p>

##  Assembly

* [Baseplate](../../CAD/ASSEMBLY_Baseplate)
* [Linear Polarizer Cube](../../CAD/ASSEMBLY_POL_Linear_Polarizer)
* [Microscope Slide Holder Cube](../../CAD/ASSEMBLY_CUBE_Mirror_Kinematic_45) : Brewster Angle Cube has same assembling procedure with Kinematic Mirror Holder 45 degrees.
* [LASER Holder Cube](../../CAD/ASSEMBLY_CUBE_Laser)   
__*EXTRA MODULES:*__
* [Sample Holder for Screen](../../CAD/ASSEMBLY_CUBE_Sample_Holder)

All necessary parts to assemble a Microscope Slide Glass Holder Module be gathered in the image below:

<p align="center">

</p>

##  Results

Brewster's angle experiment setup can be prepared easily. After printing and assembling the module parts, we try to find a critical angle or Brewster's angle as much as we can.

<p align="center">

</p>

In this setup, we use LASER as a light source because it is easier to observe the polarization degree changes by reflection. As a first step, LASER light beams reflect from microscope slide glass and pass through a linear polarizer. Then a piece of paper is inserted on the sample holder comb. Finally, we can observe the totally polarized reflected light.

<p align="center">

</p>

We should make a good alignment to find the Brewster angle as the incidence angle of the incoming light. In practice, it is hard because of using screws, we could not find the exact incidence angle of a microscope slide. Nevertheless, I could take results that are almost perfectly polarized light after reflection in almost critical angle.   
You can see the reflected laser light beam without alignment at a random incident angle above.

In the image below, the incoming beam is reflected with almost Brewster angle, 57 degrees for microscope slide glass:

<p align="center">

</p>

Let's look at our almost perfectly polarized light by reflection experiment video records. The orientation direction of the linear polarizer only changes in 1st and 2nd videos, and we see that reflected light is totally polarized almost.  The light is blocked, and we can see almost no light after the polarizer when the orientation of the linear polarizer is perpendicular to the polarization orientation of the reflected beam.

<p align="center">

</p>

<p align="center">

</p>

## New Ideas
We are open to new ideas. Please contribute to the project freely, this place is a free country which is built by codes and machines :robot:

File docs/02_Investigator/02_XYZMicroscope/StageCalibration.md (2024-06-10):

# Stage Mapping and Stage Calibration

## Stage Coordinates

In this tutorial, we will guide you through the process of aligning the coordinate systems for the UC2 microscope stage. Proper alignment ensures that the movement of the stage corresponds accurately with the image displayed on the screen, facilitating an intuitive user experience. In principle all of this can be handled in software (e.g. flipping the camera image, changing stage axis), but it's always good to start with a common ground from the hardware side.

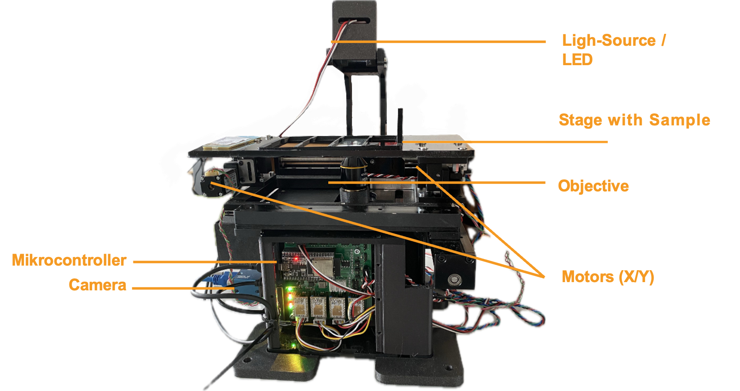
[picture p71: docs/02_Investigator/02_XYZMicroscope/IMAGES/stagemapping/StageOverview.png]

*This is the microscope (UC2 XYZ v3) with the ingredients controlled by ImSwitch*

### Alignment of Axes

The goal of aligning the coordinate systems is to ensure they are correctly matched. The alignment of the stage is considered from the origin point (zero point). The desired behavior is as follows:
- When the stage moves to the right (x+), the image on the screen should also move to the right.
- When the stage moves upwards (y+), the image on the screen should move upwards as well.

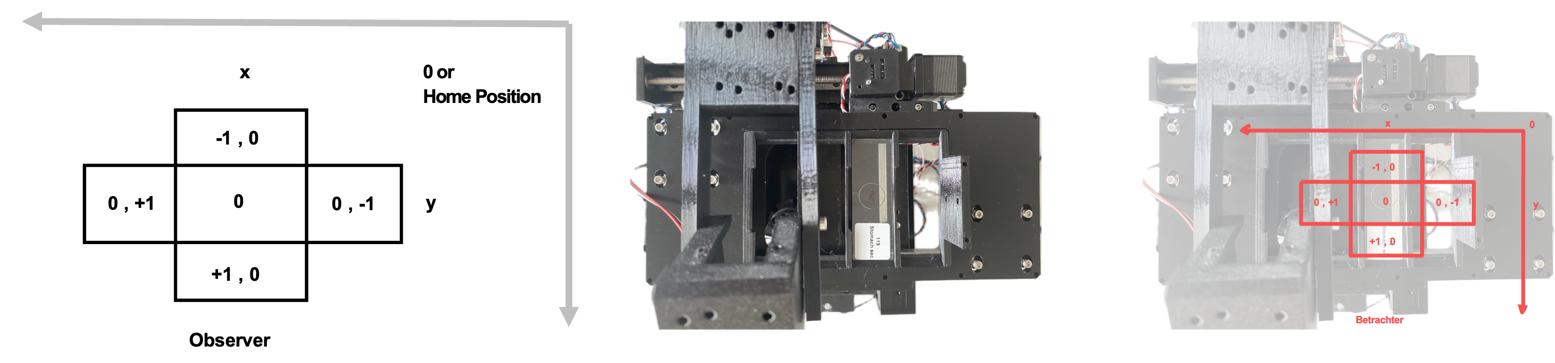
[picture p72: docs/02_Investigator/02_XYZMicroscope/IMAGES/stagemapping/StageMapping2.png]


This is illustrated in the following Figure. When viewing the sample from above with the microscope positioned in front, the image should match what is shown in Imswitch.
This is also represented by the `VirtualMicroscope` with the `VirtualStage` and `VirtualCamera` in this config (Config: https://github.com/openUC2/ImSwitchConfig/blob/master/imcontrol_setups/example_virtualmicroscope.json).

### Understanding Axes in NumPy

It's important to note the labeling of axes. In NumPy, x = 1 and y = 0. This means:
- The x-axis is the second axis (index 1) of an array.
- The y-axis is the first axis (index 0) of an array.

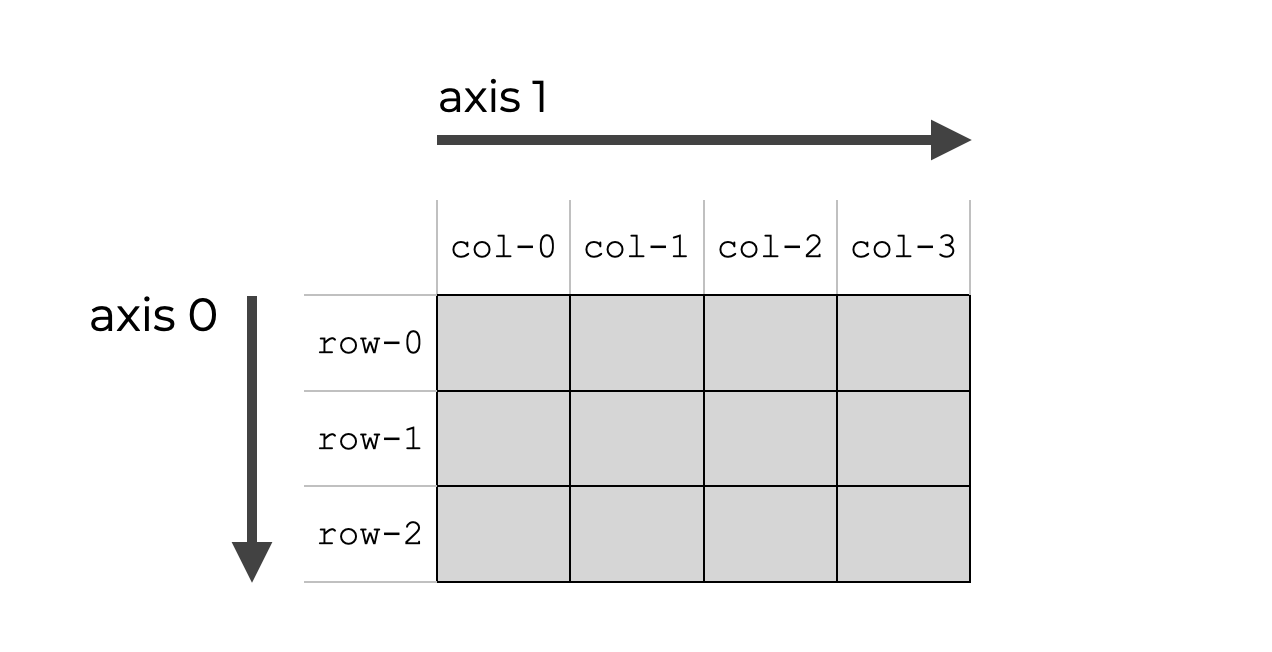
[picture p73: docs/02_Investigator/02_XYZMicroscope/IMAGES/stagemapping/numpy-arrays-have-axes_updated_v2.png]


NumPy arrays are multidimensional, with axes numbered as follows:
- Axis 0 is the first axis (often the vertical direction).
- Axis 1 is the second axis (often the horizontal direction).

### Stage Coordinate System

When viewing the stage from above, the coordinate system is arranged as follows:

- **X-Axis (Horizontal)**
  - Positive direction: Right
  - Negative direction: Left
- **Y-Axis (Vertical)**
  - Positive direction: Up
  - Negative direction: Down

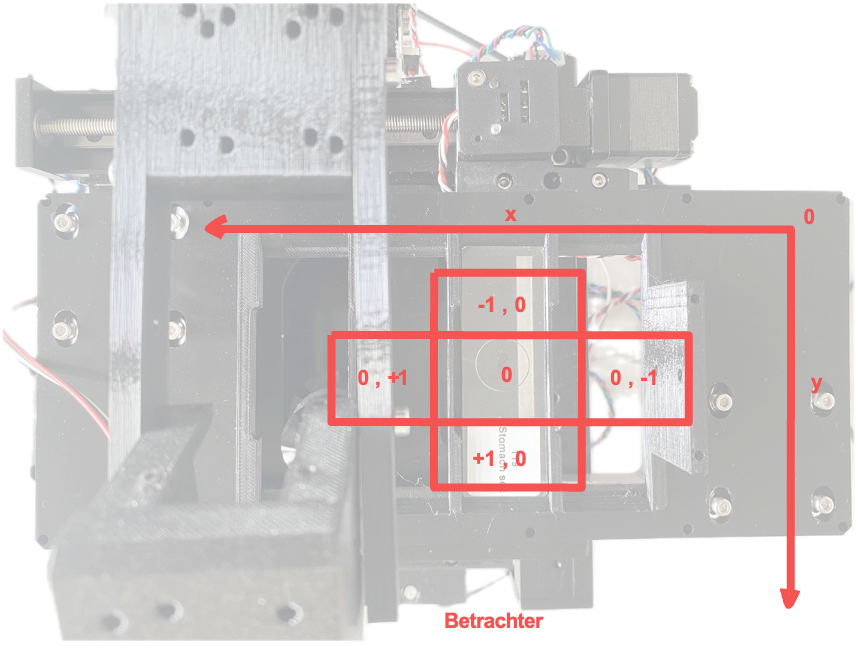
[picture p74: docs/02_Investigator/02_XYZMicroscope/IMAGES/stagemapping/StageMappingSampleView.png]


### Aligning Axes with Imswitch

To enable intuitive operation, the stage and camera axes must be correctly aligned with the coordinate system in Imswitch. To achieve this, the commands "flip x" and "flip y" are used. These commands invert the direction of the axes in the coordinate system, meaning that movement or position along the axes is reversed.

#### Steps for Aligning Axes:

1. **Initial Setup:**
   - Ensure the microscope and stage are properly connected to the control software (e.g., Imswitch).

2. **Define Origin:**
   - Identify the origin (zero point) of the stage coordinate system. (in Hardware this would be defined by the Endstops that are used for homing the axes; The motor will run - if the direction is set correctly - until it hits the switch)

3. **Test Movement:**
   - Move the stage to the right and observe the direction of the image on the screen.
     - If the image moves left, apply the "flip x" command.
   - Move the stage upwards and observe the direction of the image on the screen.
     - If the image moves down, apply the "flip y" command.

4. **Adjust Axes:**
   - Use the following commands as needed to align the axes:
     ```python
     # Flip the x-axis if necessary
     if x_movement_incorrect:
         stage.flip_x()

     # Flip the y-axis if necessary
     if y_movement_incorrect:
         stage.flip_y()
     ```

5. **Verify Alignment:**
   - After applying the flips, verify that the stage movements correspond correctly with the image movements on the screen.

6. **Save Configuration:**
   - Save the configuration settings to ensure the alignment persists across sessions.

## Stage Calibration

Richard Bowman and his team provided a very nice way to calibrate stage coordinates to camera pixel coordinates. We burtally integrated the open-source software which you can find here: https://gitlab.com/openflexure/microscope-extensions/camera-stage-mapping into ImSwitch. If you activate the `HistoScan` Controller and Widget you can start it either by the GUI or using the HTTP interface by calling http://localhost:8002/HistoScanController/startStageMapping (URL and PORT may differ). What the stage will do is moving a certain series of steps in XY, performs a cross-correlation of the images and computes the shift in XY of the mciroscope image on the camera, compares it to the expected shift on and returns the Image-To-Stage-Displacement Matrix as well as the Backlashvector. Both matrices/vectors are microscope specificand will help you matching e.g. stage coordinates for stitching software such as ASHLAR or OFM Stitching. This document should give you a rough idea of what's happening.

Some terminology:

- **Combine X and Y calibrations**: The calibration involves combining two separate measurements or calibration runs for the x and y directions, ensuring that the directions are orthogonal (at right angles to each other).

- **2x2 transformation matrix**: The `image_to_stage_displacement` matrix maps image displacements to stage displacements. This ensures that movements in the image coordinate system are accurately translated to movements in the stage coordinate system.

- **backlash_vector**: This is a vector estimating the backlash (mechanical slack or play in the system) in each direction. In this case, the estimated backlash is zero, indicating a precise calibration with no noticeable mechanical play.

- **backlash**: The function is expected to return the highest element of `backlash_vector` as a scalar value, which would be zero in this case.

## Interpreation of the Matrix

### Calibration Matrix `image_to_stage_displacement`

The entries of the calibration matrix `image_to_stage_displacement` can be given specific names and meanings based on their positions within the matrix. Let's denote the matrix as follows:

$$
\text{image\_to\_stage\_displacement} =
\begin{pmatrix}
0 & -1.0 \\
-1.0 & 0
\end{pmatrix}
$$
$$
\begin{pmatrix}
a & b \\
c & d
\end{pmatrix}
$$

#### Entries and Their Names

1. **a (0)**:
   - **Name:** `a`
   - **Meaning:** Represents the scaling factor from the x-coordinate in the image to the x-coordinate in the stage. Here, it is 0, indicating no direct mapping from image x to stage x.

2. **b (-1.0)**:
   - **Name:** `b`
   - **Meaning:** Represents the scaling factor from the y-coordinate in the image to the x-coordinate in the stage. The value -1.0 indicates an inverse and slightly scaled mapping from image y to stage x.

3. **c (-1.0)**:
   - **Name:** `c`
   - **Meaning:** Represents the scaling factor from the x-coordinate in the image to the y-coordinate in the stage. The value -1.0 indicates an inverse and slightly scaled mapping from image x to stage y.

4. **d (0)**:
   - **Name:** `d`
   - **Meaning:** Represents the scaling factor from the y-coordinate in the image to the y-coordinate in the stage. Here, it is 0, indicating no direct mapping from image y to stage y.

### Summary of the Matrix Entries

- **a (0)**: No direct mapping from image x to stage x.
- **b (-1.0)**: Inverse mapping from image y to stage x.
- **c (-1.0)**: Inverse mapping from image x to stage y.
- **d (0)**: No direct mapping from image y to stage y.

This calibration matrix indicates that there is a transformation involving a 90-degree rotation combined with an inverse scaling factor slightly above 1 between the image coordinates and the stage coordinates. The exact interpretation may depend on the specific application, but generally, it implies that movements in one direction in the image are mapped to movements in the perpendicular direction on the stage with a slight scaling adjustment.

## Interpretation of the Values

The following simulation of the `VirtualMicroscope` inside ImSwitch (Config: https://github.com/openUC2/ImSwitchConfig/blob/master/imcontrol_setups/example_virtualmicroscope.json):

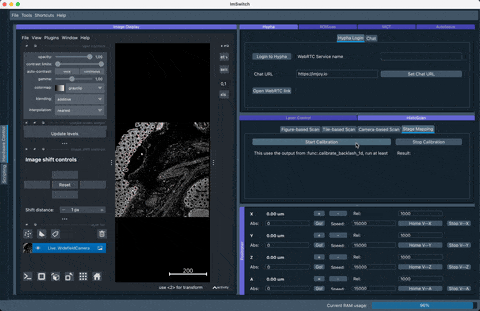
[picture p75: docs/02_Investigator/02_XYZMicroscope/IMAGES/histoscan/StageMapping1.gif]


The result of the stage mapping is a json file containing (under `/ImSwitch/calibFile.json`) the following important element:

```json
    "camera_stage_mapping_calibration": {
        "backlash": 0.0,
        "backlash_vector": [
            0.0,
            0.0,
            0.0
        ],
        "image_to_stage_displacement": [
            [
                0.0,
                -1.0
            ],
            [
                -1.0,
                0.0
            ]
        ]
    }
```

The provided matrices explains transforming image coordinates to stage coordinates and estimating backlash. Let's break down the interpretation of the entries:

### 1. `image_to_stage_displacement` Matrix

```python
mData["camera_stage_mapping_calibration"]["image_to_stage_displacement"] =
array([[ 0.        , -1.00135997],
       [-1.00135997,  0.        ]])
```

This matrix is a 2x2 transformation matrix used to map image coordinates to stage coordinates. Each entry in this matrix has a specific meaning:

- **\[0,0\] = 0**: There is no direct transformation of the x-coordinate in the image to the x-coordinate in the stage.
- **\[0,1\] = -1.00135997**: The y-coordinate in the image inversely affects the x-coordinate in the stage.
- **\[1,0\] = -1.00135997**: The x-coordinate in the image inversely affects the y-coordinate in the stage.
- **\[1,1\] = 0**: There is no direct transformation of the y-coordinate in the image to the y-coordinate in the stage.

The presence of -1.00135997 off-diagonal elements indicates that the transformation involves a negative and approximately unit scaling between the coordinates, implying a possible 90-degree rotation combined with a scaling factor close to -1.

### 2. `backlash_vector` Matrix

```python
mData["camera_stage_mapping_calibration"]["backlash_vector"] =
array([ 0.,  0.,  0.])
```

This vector represents the estimated backlash in each direction (x, y, and possibly z, though z is not utilized in a 2D context). Here, all elements are zero, indicating no measurable backlash in the x and y directions.

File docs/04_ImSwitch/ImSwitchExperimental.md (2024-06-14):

# ImSwitch Experimental Features Documentation

## Overview

This document details the new experimental features for the microscopy control software, ImSwitch. These features include a headless version of the software, suitable for resource-constrained environments, and a Docker container setup for easy deployment and testing.
The headless version allows operation on resource-limited devices, while the Docker container facilitates easy deployment and testing. Please provide feedback and report any issues encountered to help improve these experimental features.

## Headless Version in Google Colab

We have developed a headless version of ImSwitch that operates without the need for the QT graphical interface. This version allows remote control and UI element access solely through the REST API or Jupyter Notebook. Please note that some functions are still under development, and this version is experimental.

### Use Cases

This headless version is particularly useful on devices such as Raspberry Pis and Nvidia Jetsons, which may struggle with the resource demands of installing and running PyQT.

### Getting Started in Google Colab

To try the headless version of ImSwitch in Google Colab, follow these steps:

1. Install ImSwitch:
    ```python
    !pip install https://github.com/openUC2/ImSwitch/archive/refs/heads/NOQT.zip #--no-deps ##--force-reinstall
    ```

2. Access the public version in Google Colab:
    [Google Colab Link](https://colab.research.google.com/drive/1fGskyp6spnU-aaYUl5Ypn2k9MvtZMN6L?usp=sharing)

3. Clone the repository and checkout the `NOQT` branch:
    ```python
    %cd ~
    !git clone https://github.com/openUC2/ImSwitch
    !git pull
    %cd ./ImSwitch
    !git checkout NOQT
    ```

4. Install the package:
    ```python
    !pip install -e .
    ```

5. Configure and run ImSwitch in headless mode:
    ```python
    from google.colab.output import eval_js
    print(eval_js("google.colab.kernel.proxyPort(8002)"))
    from imswitch.__main__ import main
    import imswitch
    imswitch.IS_HEADLESS = True
    main(is_headless=True, default_config="example_virtual_microscope.json")
    input()  # Prevent from closing the cell
    ```

## Docker Container

A Docker container is available for ImSwitch, providing a convenient way to deploy and test the software.

### Docker Container Details

- **Container Registry:** [ImSwitch Container Registry](https://github.com/openUC2/ImSwitch/pkgs/container/imswitch)
- **Docker Pull Command:**
    ```sh
    docker pull ghcr.io/openuc2/imswitch:latest
    ```

- **Dockerfile:** [ImSwitch Dockerfile](https://github.com/openUC2/ImSwitch/blob/master/docker/dockerfileImSwitch)

### Running the Docker Container

1. Launch the Docker container:
    ```sh
    docker run -it --rm -p 9876:9876 -p 8001:8001 -p 2222:22 imswitch
    ```

2. Access the GUI and REST API:
    - Open your browser and go to `localhost:9876` to access the GUI.
    - Go to `localhost:8001` to access the REST API.

### Notes

- This Docker setup is primarily a demo version to freeze system dependencies.
- The next step involves integrating actual hardware for complete functionality.

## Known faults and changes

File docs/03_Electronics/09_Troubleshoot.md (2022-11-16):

---
id: uc2e9
title: Replace Hardware
---

### ❌ Replacing parts
Duration:1

It can happen that either the ESP32 Dev Kit or one of the motor driver fails due to ESD. You can find alternatives here:

- A4988 Stepper driver ([Amazon](https://www.amazon.de/AZDelivery-A4988-Schrittmotor-Treiber-Modul-Parent/dp/B07ZQHN62Q))
- ESP32 Dev Kit ([Amazon](https://www.amazon.de/AZDelivery-Development-Compatible-Including-Successor/dp/B07Z83MF5W/ref=sr_1_2_sspa?crid=2VAY9L1U49HOM&keywords=ESP32+dev+kit&qid=1666383153&qu=eyJxc2MiOiI0LjAxIiwicXNhIjoiMy43NCIsInFzcCI6IjMuMzYifQ%3D%3D&s=industrial&sprefix=esp32+dev+kit%2Cindustrial%2C260&sr=1-2-spons&psc=1&smid=A1X7QLRQH87QA3))

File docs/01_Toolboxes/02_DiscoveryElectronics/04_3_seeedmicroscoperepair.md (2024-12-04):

# openUC2 Xiao AI Microscope Troubleshooting )

## Flashing the ESP32S3 in case the bootloader is not responding

Sometimes - with a wrong firmware, one can not simply flash a new firmware. One has to press the boot/reset buttons to bring the ESP32S3 xiao into boot mode. It's a bit unfortunate that there is no workaround to do that via Software. So we would need to access the tiny buttons of the MCU. For this we have to open the device. Don't worry, it's doable and worth it! According to seeed studio, there is no way to determine when the firmware can easily be flashed or needs a manual enter into the bootloader.

:::error
We found out that you can bypass the reset/boot-button holding sequence in case the firmware has bricked the device by erasing the flash and then uploading a new firmware via our online tool. You can visit the ESP Flash Tool here: https://espressif.github.io/esptool-js/ and follow the following steps:
1. connect the board to your computer via USB
2. select your port
3. select erase flash and hit start

This removes everything from the device's flash. Then proceed to flash your favourite firmware from e.g. from our repo: https://matchboxscope.github.io/firmware/FLASH.html

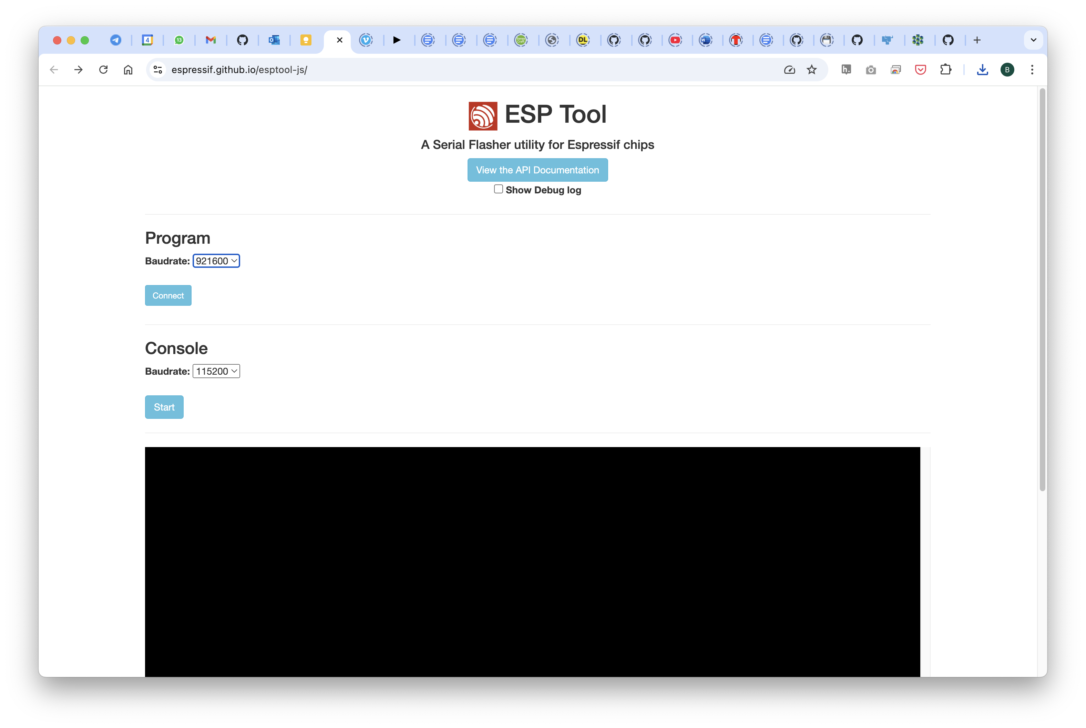
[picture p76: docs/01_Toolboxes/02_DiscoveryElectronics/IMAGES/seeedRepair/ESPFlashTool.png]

:::

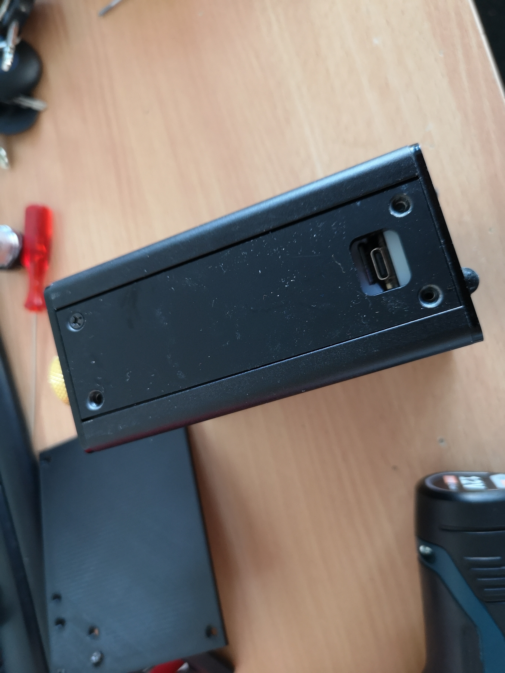
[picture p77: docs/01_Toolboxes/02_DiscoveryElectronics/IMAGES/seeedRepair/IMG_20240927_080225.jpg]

*Open the device by unscrewing all panels using philips screwdrivers*

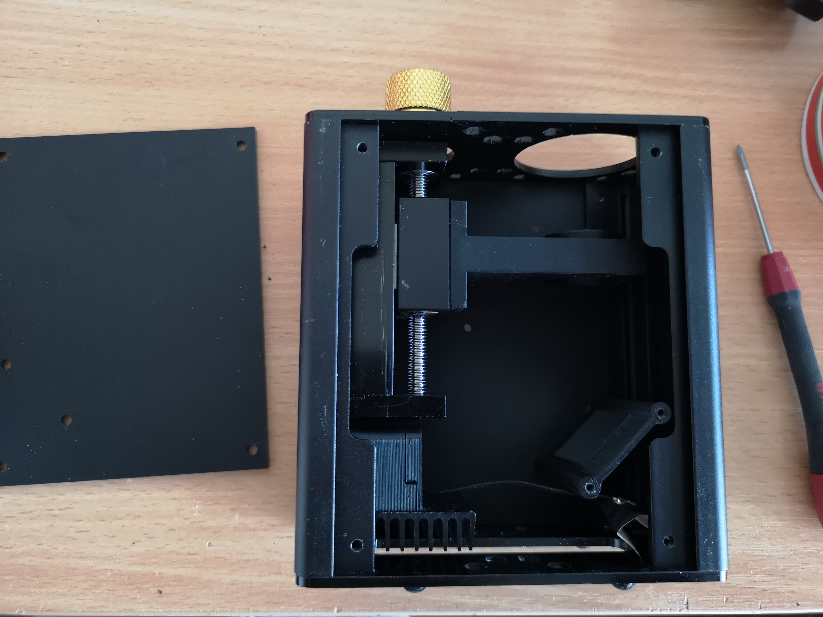
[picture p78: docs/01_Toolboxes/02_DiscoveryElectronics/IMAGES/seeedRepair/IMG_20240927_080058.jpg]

*remove the lens (optional)*

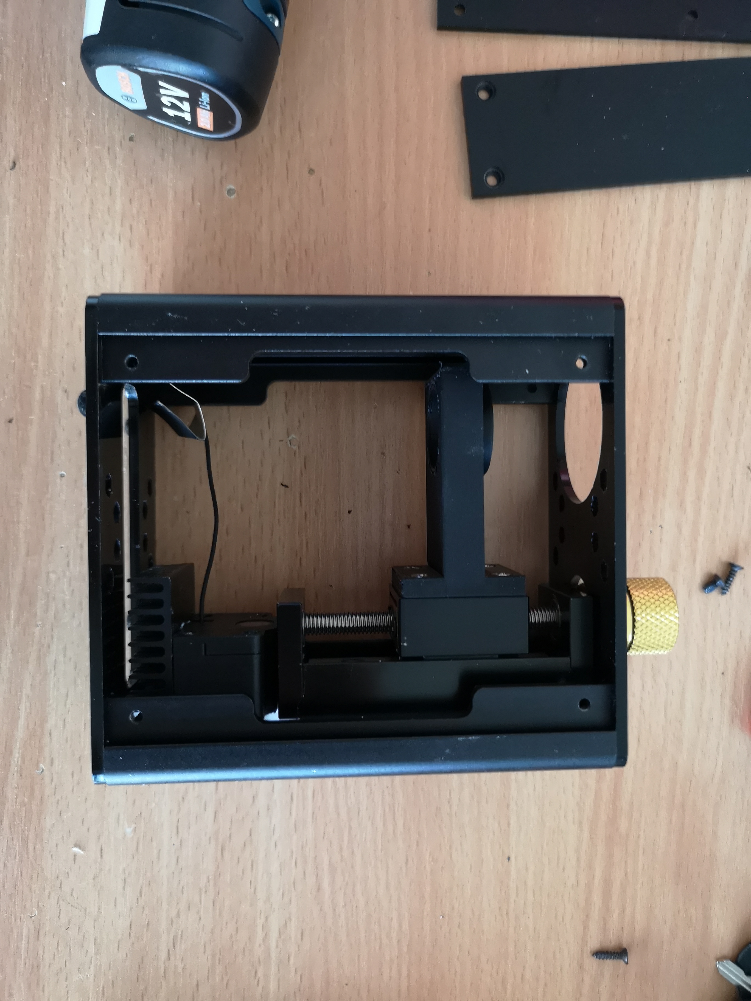
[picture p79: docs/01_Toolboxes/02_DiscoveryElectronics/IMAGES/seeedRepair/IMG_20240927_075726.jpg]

*all panels removed*

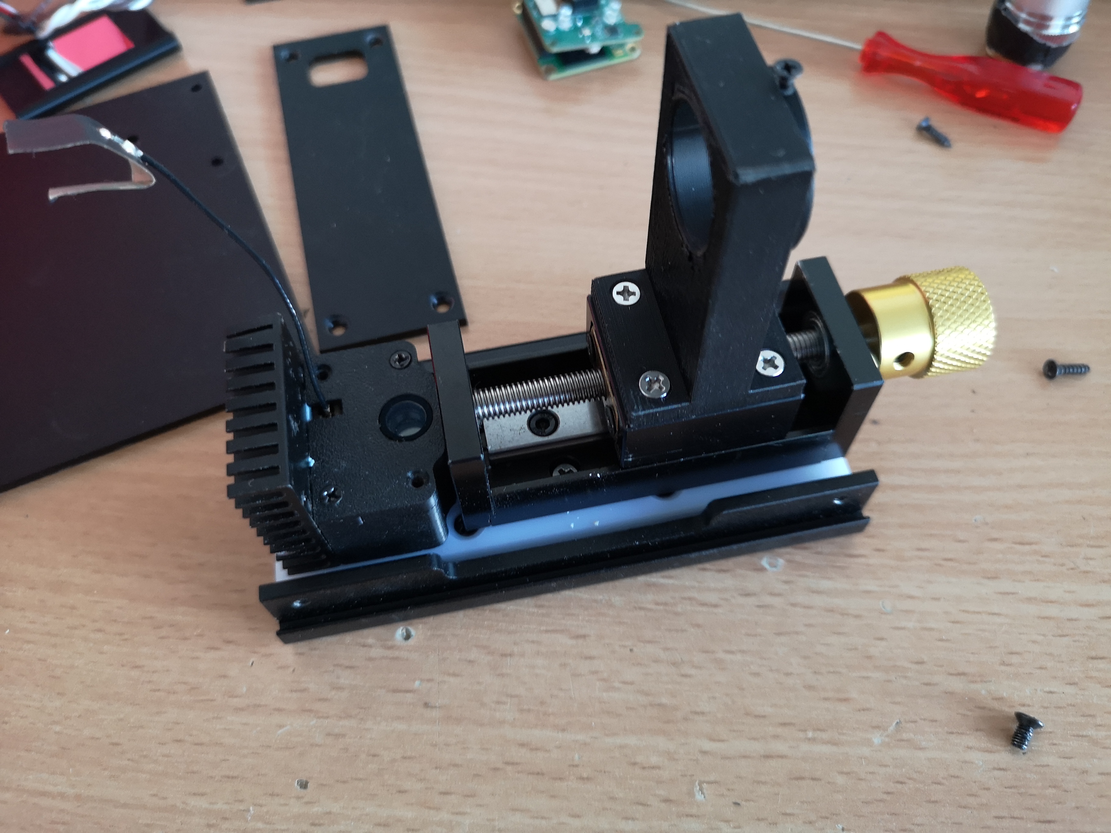
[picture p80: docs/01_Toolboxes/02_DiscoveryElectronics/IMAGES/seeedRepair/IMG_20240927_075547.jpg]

*unscrew the side where the z-stage remains*

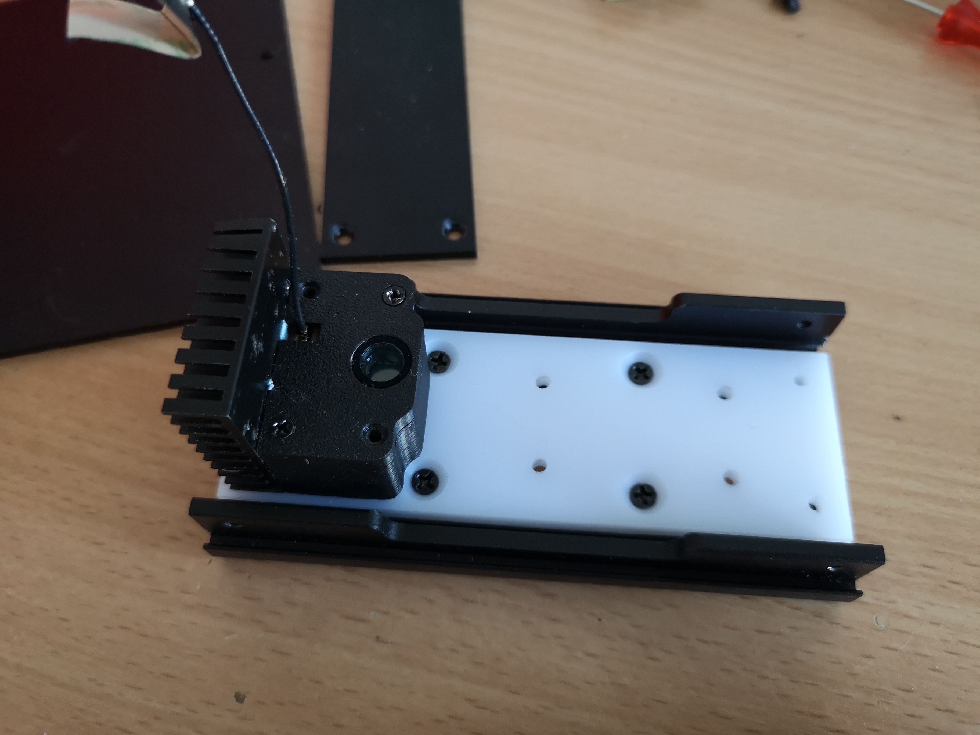
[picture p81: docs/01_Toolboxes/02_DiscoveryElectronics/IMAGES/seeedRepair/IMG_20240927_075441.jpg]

*this is the camera module, remove the z-stage*

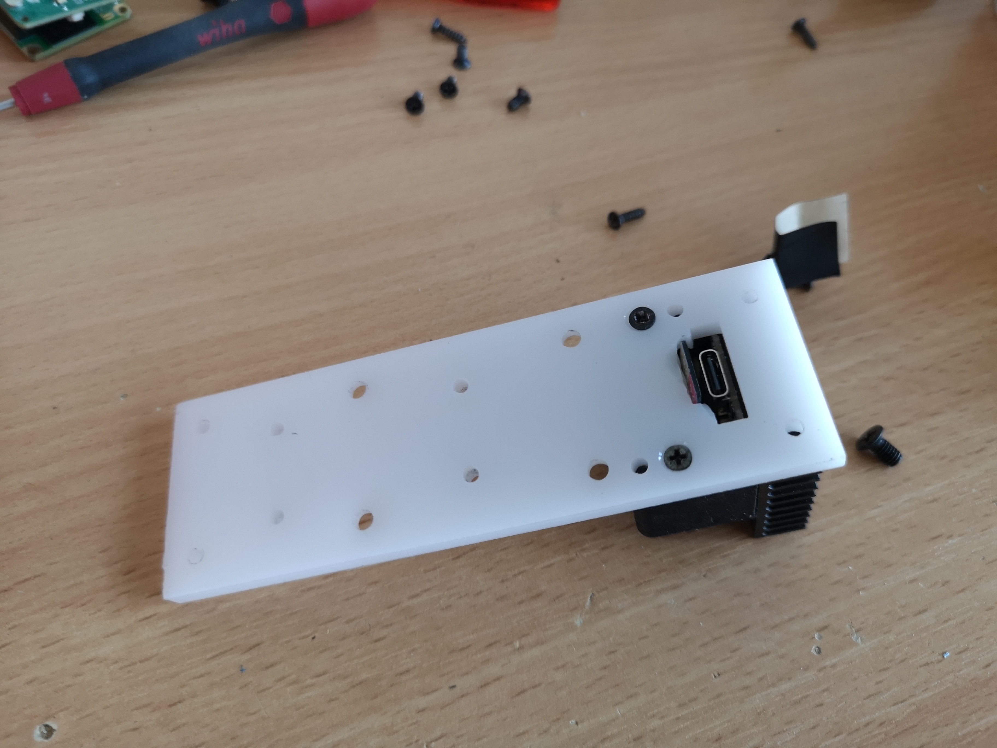
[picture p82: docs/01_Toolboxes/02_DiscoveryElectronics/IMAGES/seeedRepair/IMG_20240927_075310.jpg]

*we need to access these two philips screws and remove the camera module from the backplate*

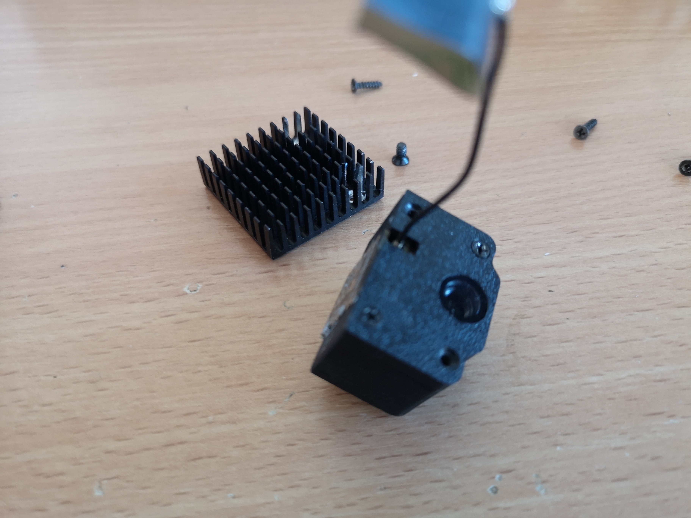
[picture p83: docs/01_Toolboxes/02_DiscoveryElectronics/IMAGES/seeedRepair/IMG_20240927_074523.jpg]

*this is the camera module, remove the cooling body*


*remove the cooling body with these two screws*


*carefully remove the cooling body and access the xia. Now you can flash it according the manual in the [Xiao Tutorial](./01_Toolboxes/02_DiscoveryElectronics/04_1_seeedmicroscope.md)

**Ensure the firmware runs, then put everything back together again. If you have questions visit our forum: https://openuc2.discourse.group

## Changing the Objective Lens

The device has a finite corrected microscope lens with an RMS thread. The design of the z-stage offers to change the lens. The mechanism has a little cap that holds the lens in place. This has to be unthreaded. Unfortunatley this is not very easy to accomplish with a closed enclosure. You simply need to remove the side plates and unscrew the cap to free the lens. The images below will help you to do so:


*Remove screws on both sides*


*remove the panels*


*unscrew this little plastic ring*


*fully unscrew it and remove the lens*


*be careful not to touch it*


*add a new lens and tighten the cap by screwing it again*


*almost done: add the panels*

## Improving the Wifi Strengths

According to SeeedStudio, the wifi strength (and hence the stream quality/speed) can be improved by folding the Wifi Antenna like so:



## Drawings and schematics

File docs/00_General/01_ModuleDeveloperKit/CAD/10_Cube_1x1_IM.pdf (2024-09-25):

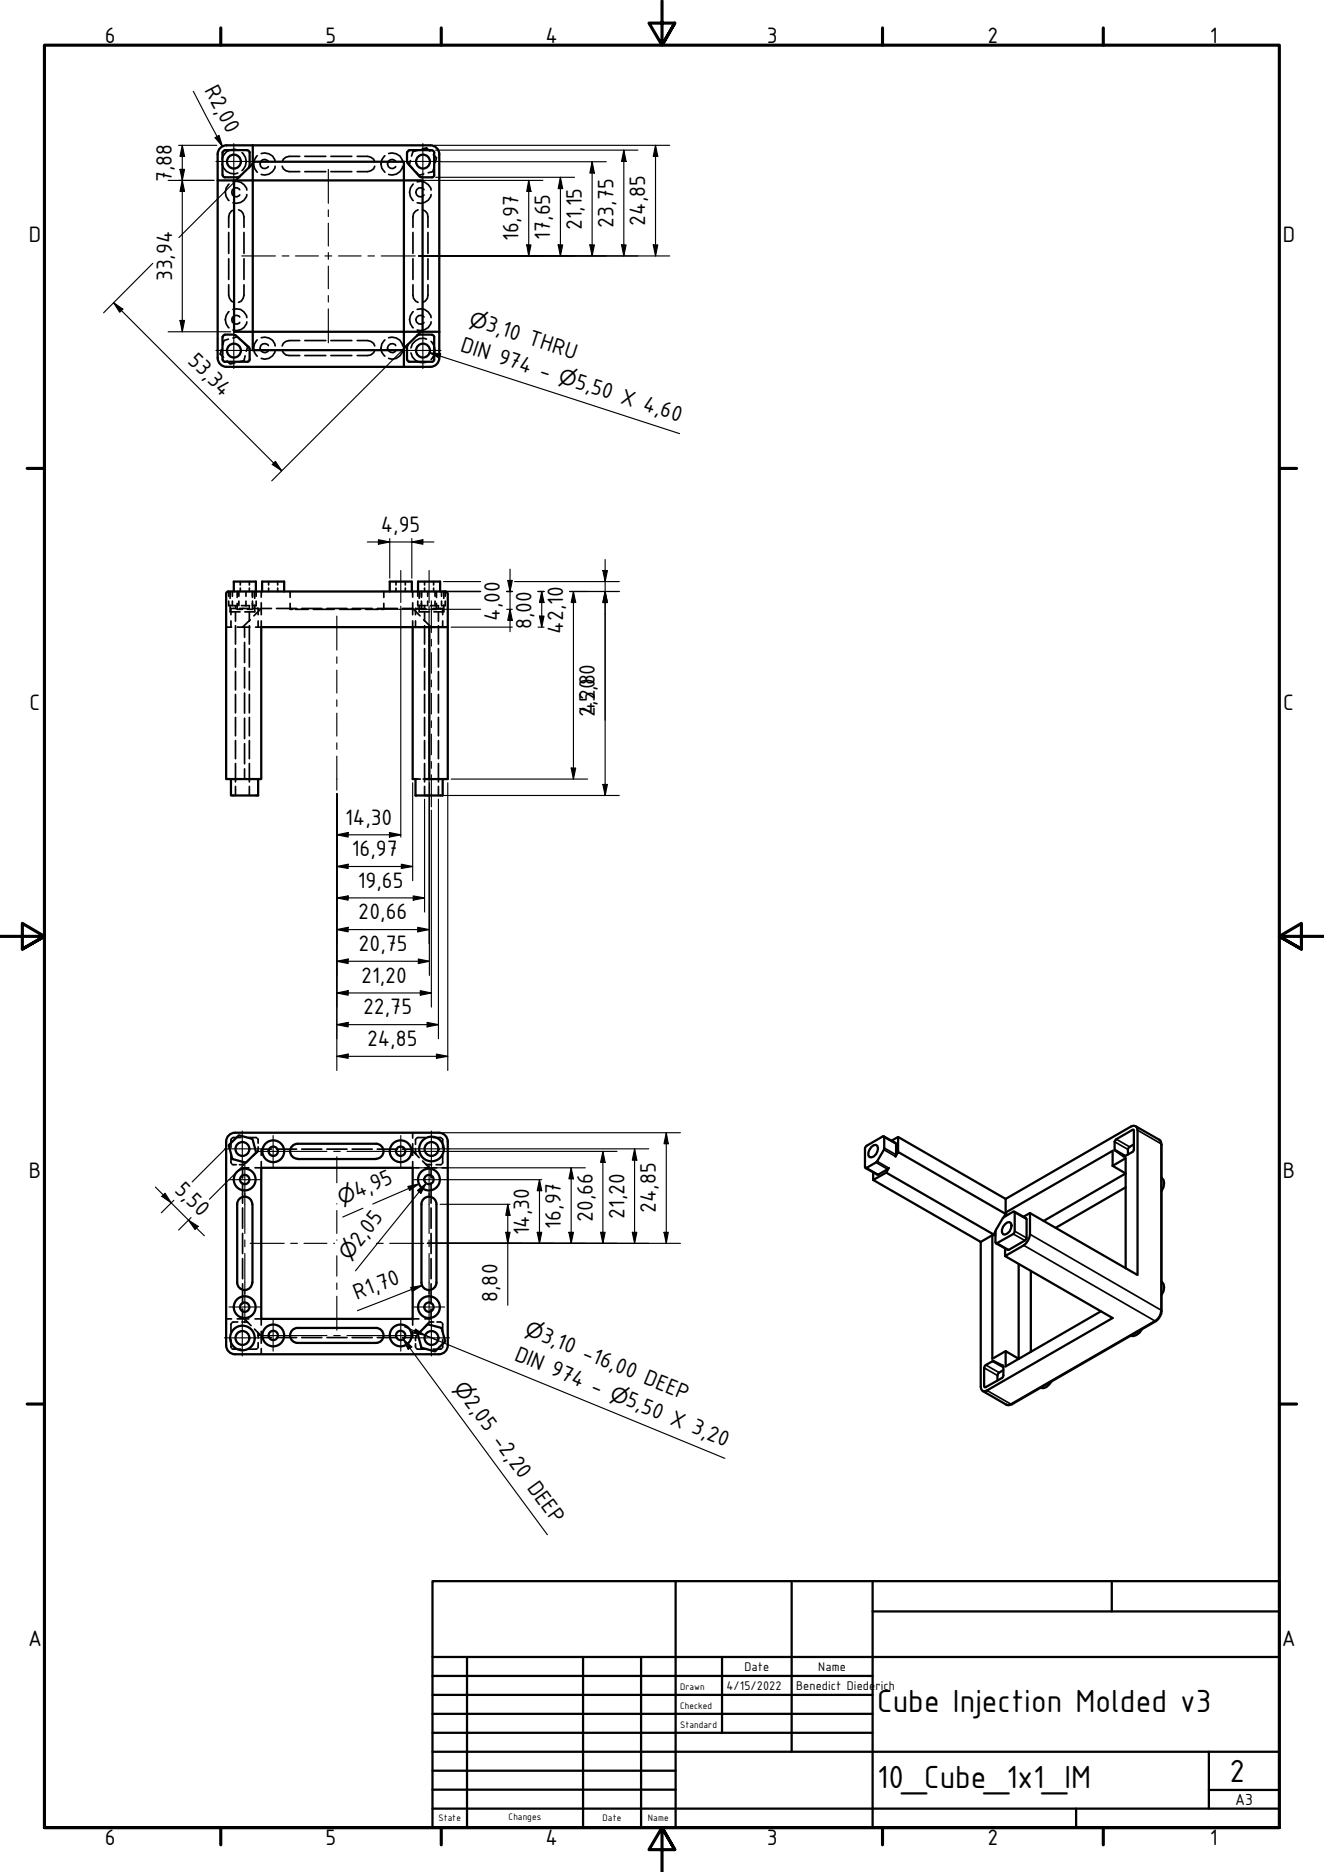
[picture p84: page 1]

Date | Name | Cube Injection Molded v3

Drawn | 4/15/2022 | Benedict Diederich

Checked

Standard

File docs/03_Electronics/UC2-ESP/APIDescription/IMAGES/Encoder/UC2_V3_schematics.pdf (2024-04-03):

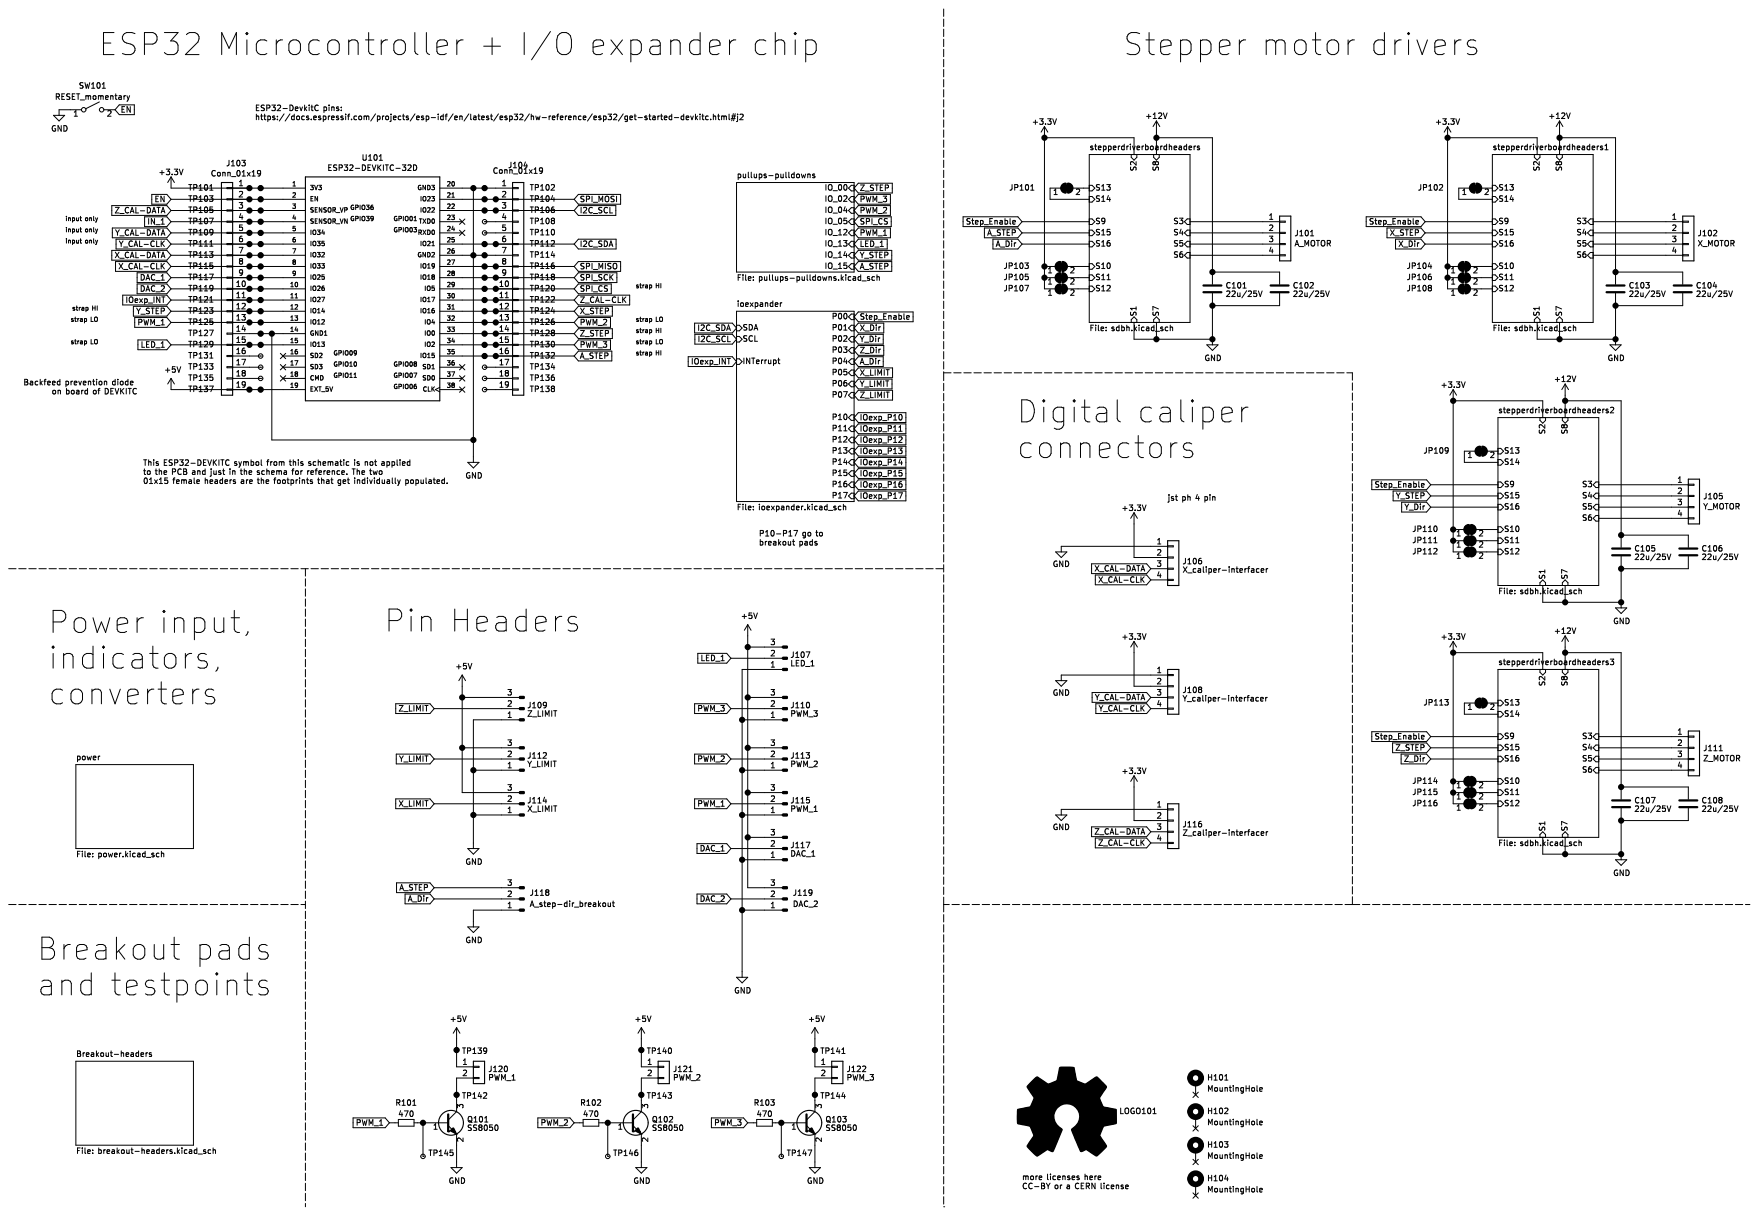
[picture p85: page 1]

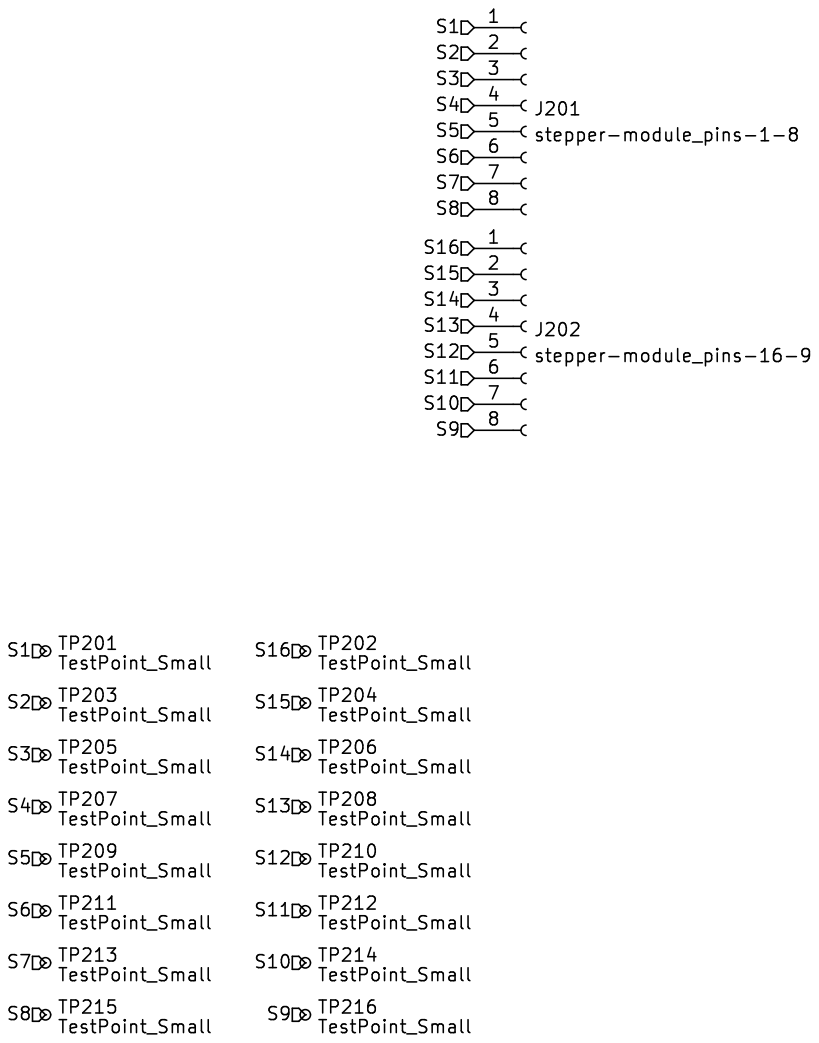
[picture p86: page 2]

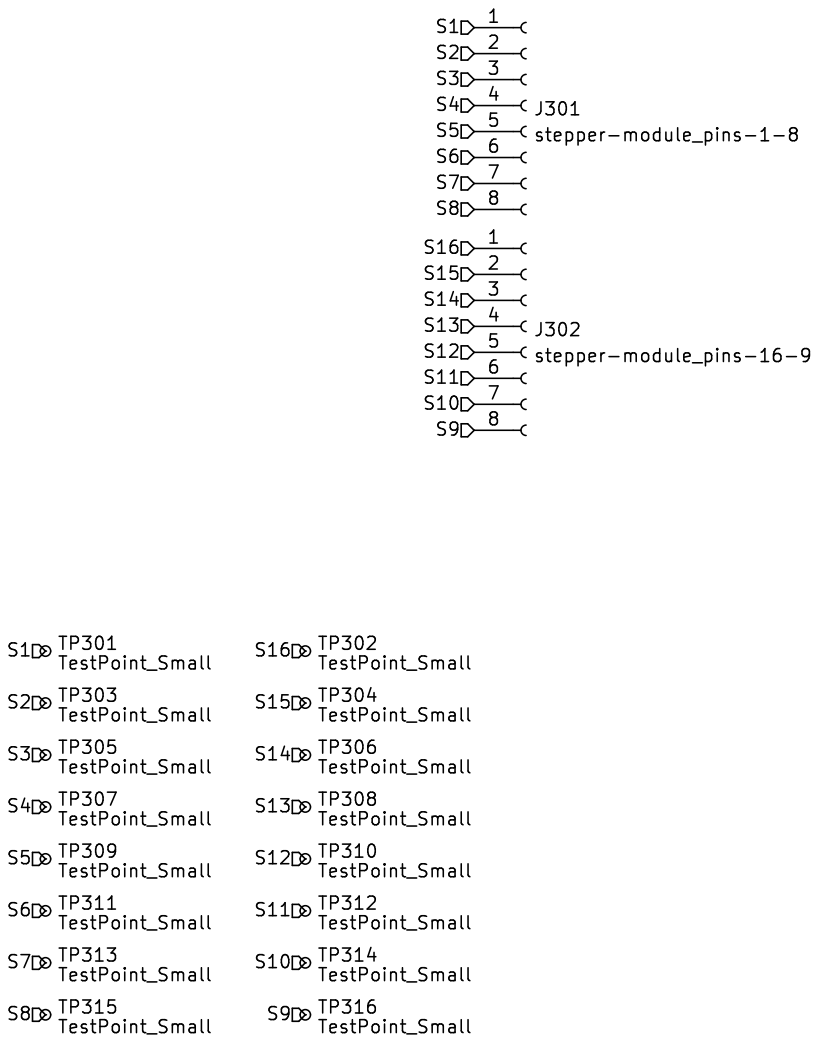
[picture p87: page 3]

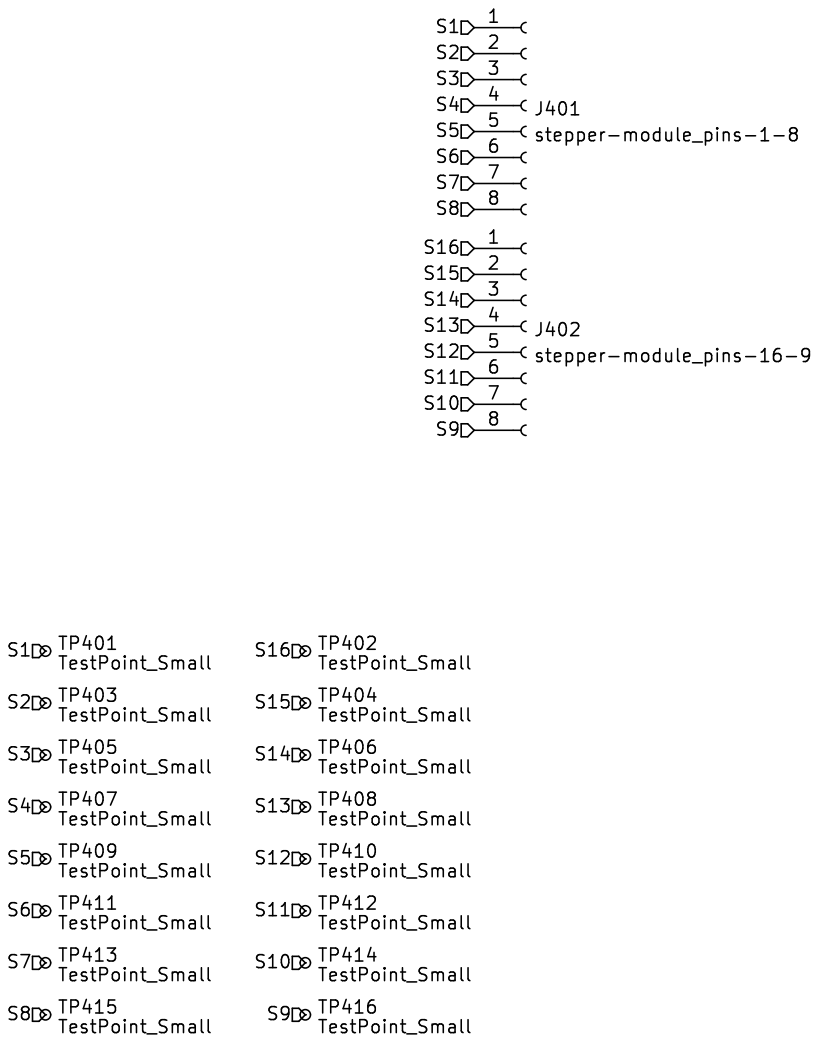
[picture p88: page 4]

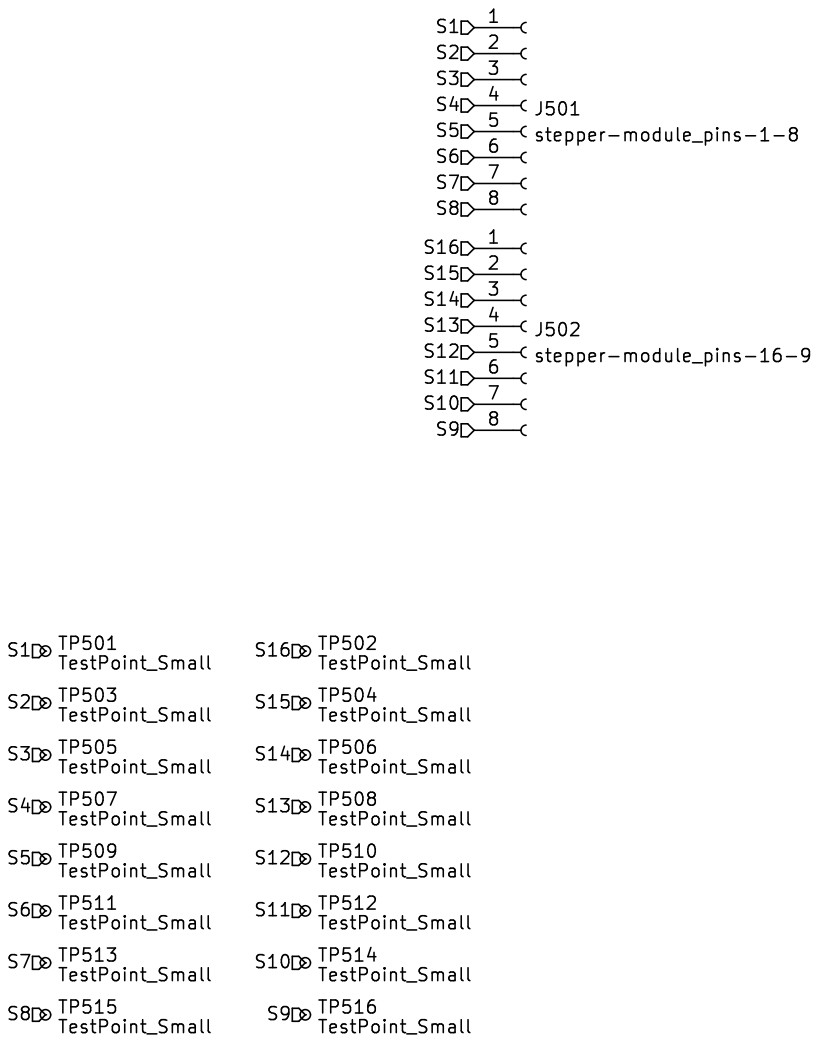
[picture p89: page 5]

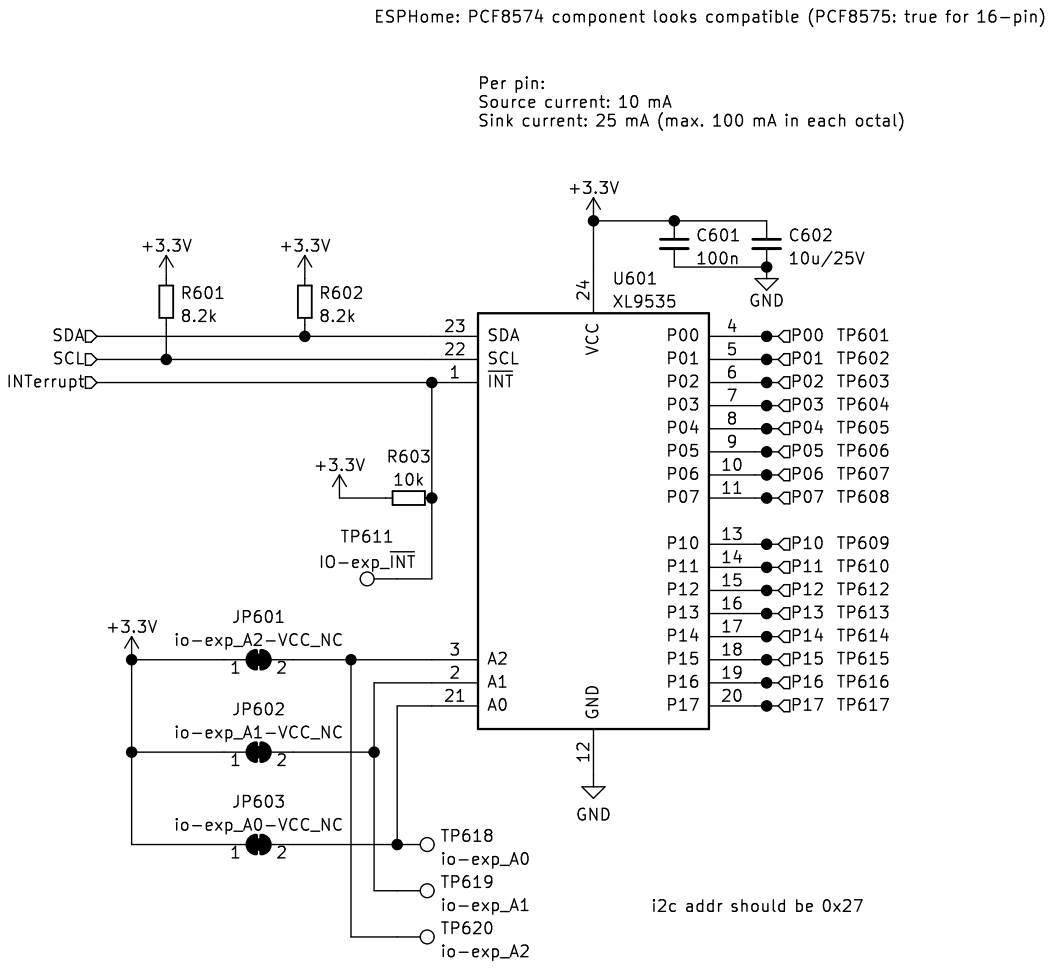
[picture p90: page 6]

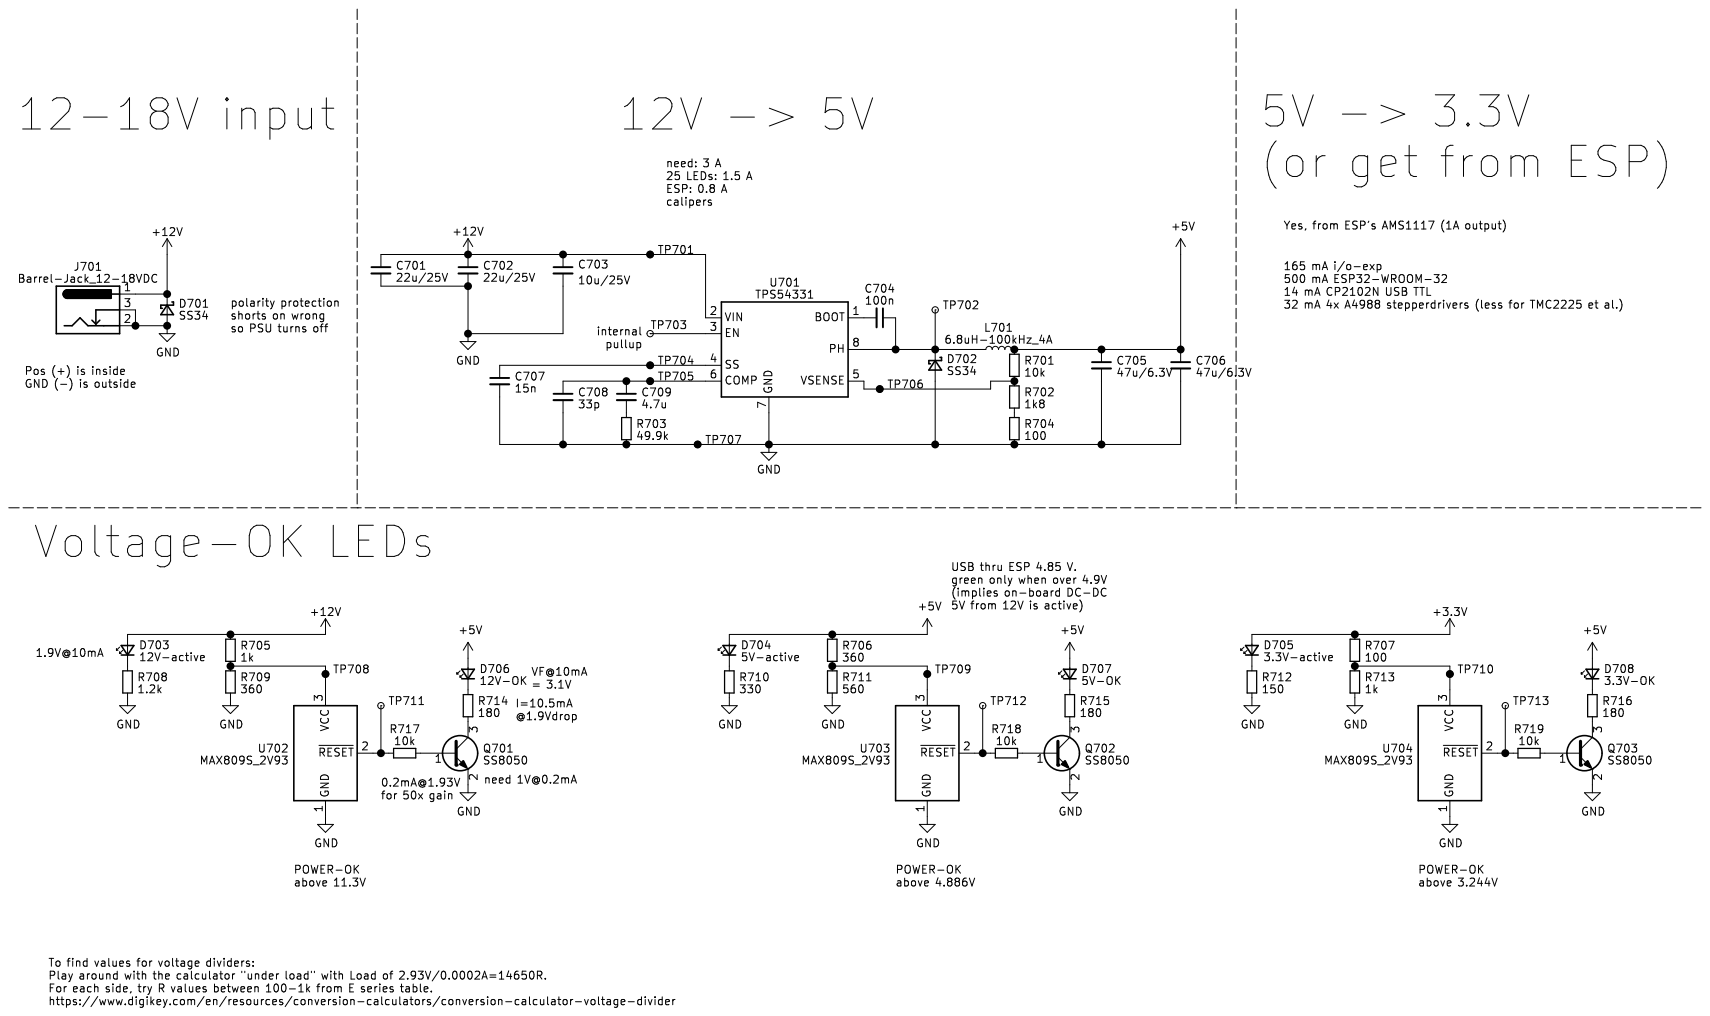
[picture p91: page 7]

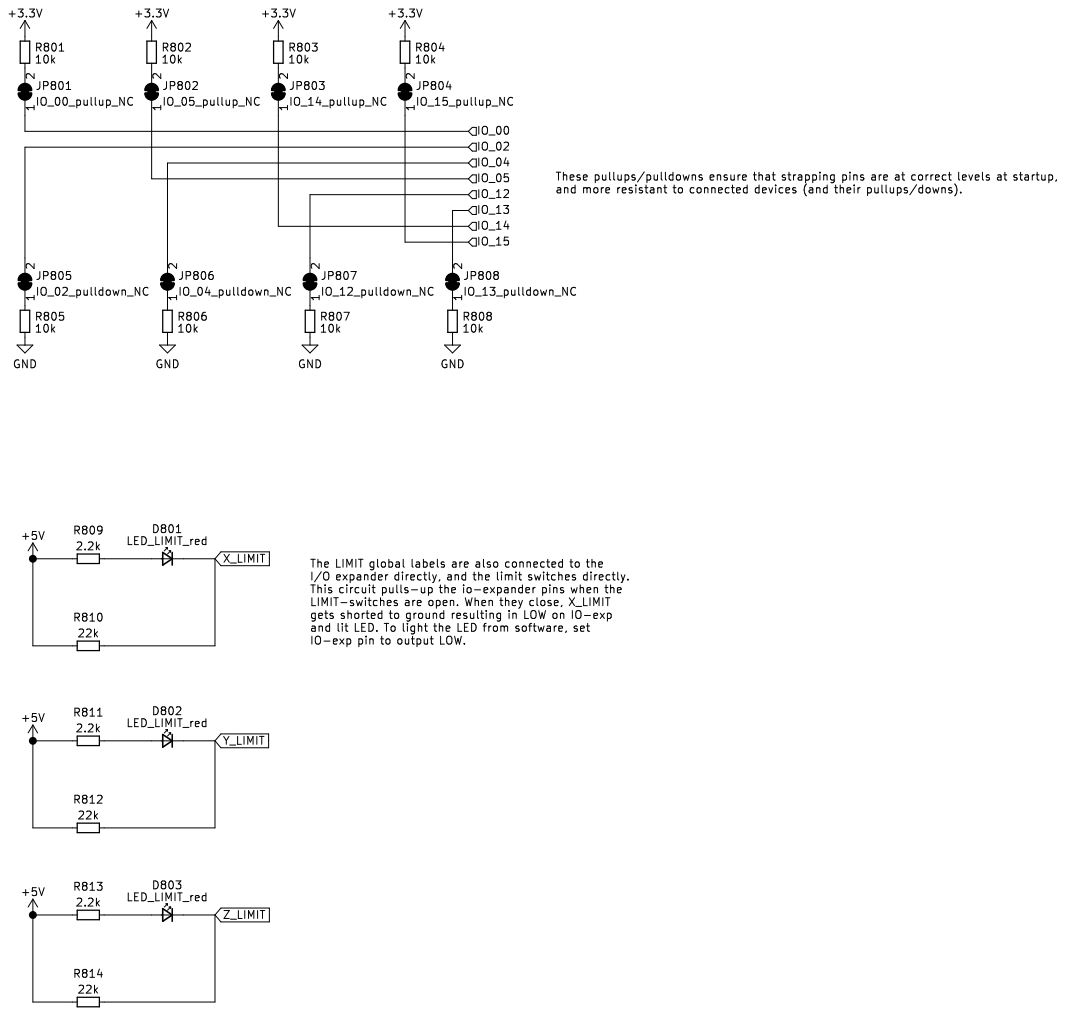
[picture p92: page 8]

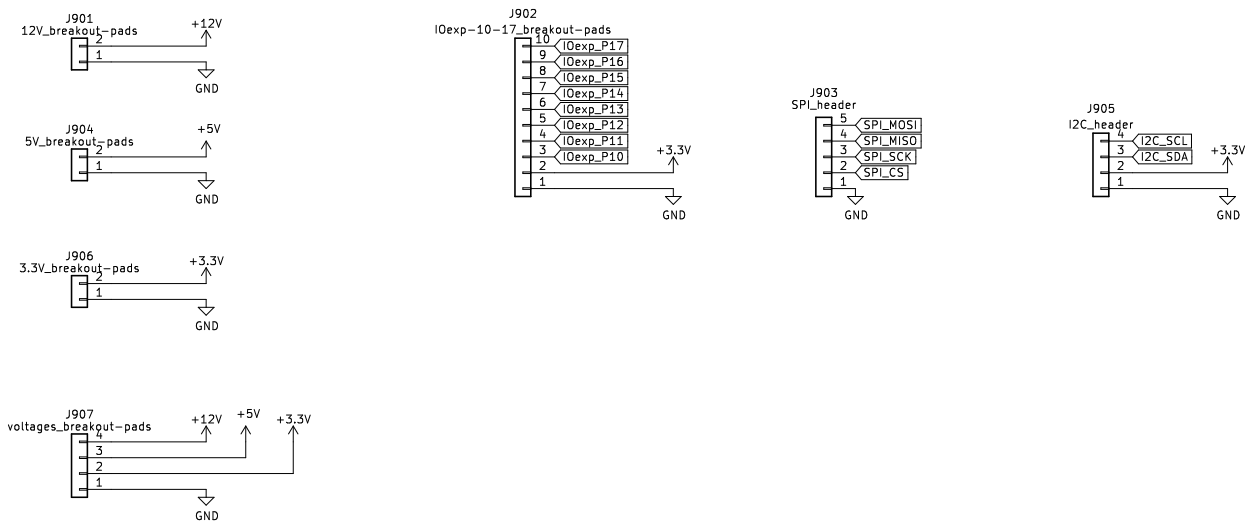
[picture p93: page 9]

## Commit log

2022-11-17 Adding Polarbox
    [00_Laser_Clamp_OnOffSwitch.stl, 10_Cube_1x1_v2.stl, 10_Lid_1x1_v2.stl, 10_Lid_el_2x1_v2.stl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]
2022-11-18 Fixing broken Image links
    [00_Laser_Clamp_OnOffSwitch.stl, 10_Cube_1x1_v2.stl, 10_Lid_1x1_v2.stl, 10_Lid_el_2x1_v2.stl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]
2022-11-18 Adding Coursebox
    [01_10_Cube_2x1_v2.stl, 02_10_Lid_el_2x1_v2.stl, 03_10_Cube_1x1_v2.stl, 04_10_Lid_1x1_v2.stl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]
2022-11-23 Adding documentation for assembly
2022-11-24 Change folder structure
    [00_Laser_Clamp_OnOffSwitch.stl, 01_10_Cube_2x1_v2.stl, 02_10_Lid_el_2x1_v2.stl, 03_10_Cube_1x1_v2.stl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]
2023-02-01 Add stage docu
2023-02-01 updating docu for stage
2023-07-27 Adding information about cameras, xyz stage and more
2023-08-08 Addings docs to mount the syringe in lightsheet
2023-09-06 Adding info about tubelens
    [TheCrown.stl]
2023-11-27 Adding resources for Spectrometer
    [02-12-2021-08:27:23.csv]
2023-12-08 ADding alignment tutorial laser
2024-04-02 Adding Motor to the Website
2024-04-04 Images update Camera tutorial
2024-06-03 adding assembly instructions for fiveD v3
2024-06-10 adding stage mapping information
2024-06-10 update the stage mapping tutorial
2024-07-01 Update and rename 02-12-2021-08:27:23.csv to 02-12-2021.csv
    rename the file to solve clone problem
    [02-12-2021.csv]
2024-07-02 Adding v3 board explanation
2024-08-06 adding docu for the xiao mnicroscopes slide + focus
    [Assembly_Cube_Linear_Sampleslide_Servo_20_Cube_Insert_linearslide_servodriven_slide_v2_8.stl, Assembly_Cube_Linear_Sampleslide_Servo_20_Cube_Insert_linearslide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]
2024-09-02 adding heat map
2024-09-25 removing OASIS, adding cube template
    [00_BallMagnets_5mm.ipt, 10_Base_puzzle_v3.ipt, 10_Base_puzzle_v3.stp, 10_Cube_1x1_IM.dwg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]
2024-10-16 Adding docs for the seeed led PCB
2024-10-16 Adding stepper backpack
2025-02-09 Add some images for the xyz stage
2025-02-11 theorie und aufbau eingefügt
2025-02-11 ImSwitch installation mit Rasberry update
    viele Fragen und commentare
2025-02-12 text angepasst und fotos eingefügt
2025-02-21 insert fotos
2025-03-03 restructuring imswitch on raspberry pi installation
2025-03-03 Anleitung für LAserFluoMicroscope
2025-03-17 wie rum verwende ich den RMS mount angepasst
2025-03-29 Adding pinouts for FRAME electronics
